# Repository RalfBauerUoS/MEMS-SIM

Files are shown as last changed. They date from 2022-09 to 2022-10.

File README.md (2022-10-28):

# MEMS-SIM
This repository is under construction and currently in development.

In the folders are details about the material list and costs to build a MEMS-SIM microscope as described in this BioRxiv preprint:  [https://www.biorxiv.org/content/10.1101/2022.09.12.507543v1](https://www.biorxiv.org/content/10.1101/2022.09.12.507543v1) 

Additionally there are 3D-designs, a basic control code specifically tailored to the MEMS used for the microscope and electronics diagram for the control.

## MEMS-SIM design
The below 3D-schematic shows the overall setup, excluting the lasers and sample stage.

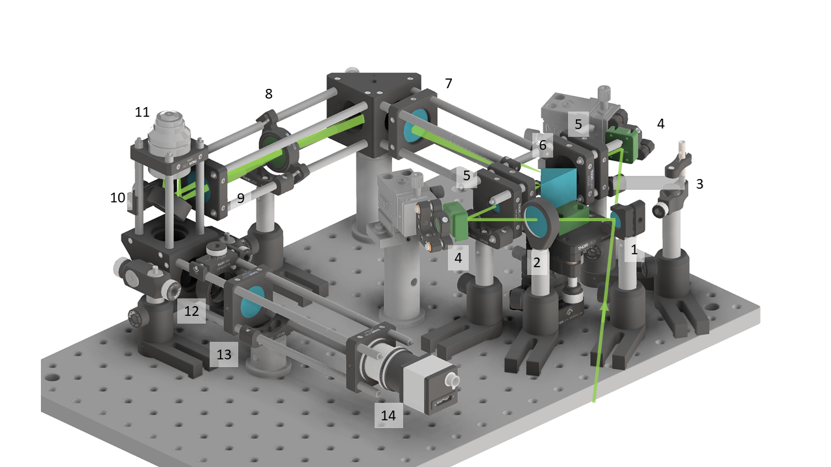
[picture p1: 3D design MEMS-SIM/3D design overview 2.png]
3D design overview


The 3D parts and full assembly of the shown setup are available in Autodesk Inventor format under the [3D design MEMS-SIM folder]

## Part list
The part list and costs (accurate as of September 2022) can be found in [this pdf](https://github.com/RalfBauerUoS/MEMS-SIM/blob/3ace88392d8fb00135eca98648ba5507b43cb822/MEMS-SIM%20-%20component%20list%20and%20costs.pdf)

## Electronics
An overview schematics of the electronics required to drive the two MEMS micromirror of the MEMS-SIM setup can be found [here](https://github.com/RalfBauerUoS/MEMS-SIM/blob/3ace88392d8fb00135eca98648ba5507b43cb822/Electronics/MEMS-SIM_Electronics_overview.png).

## MEMS control
The tip, tilt and piston movement and positioning of the two MEMS micromirror is controlled using an Arduino micro and custom python code with GUI. Both can be found in the relevant sub-folder.

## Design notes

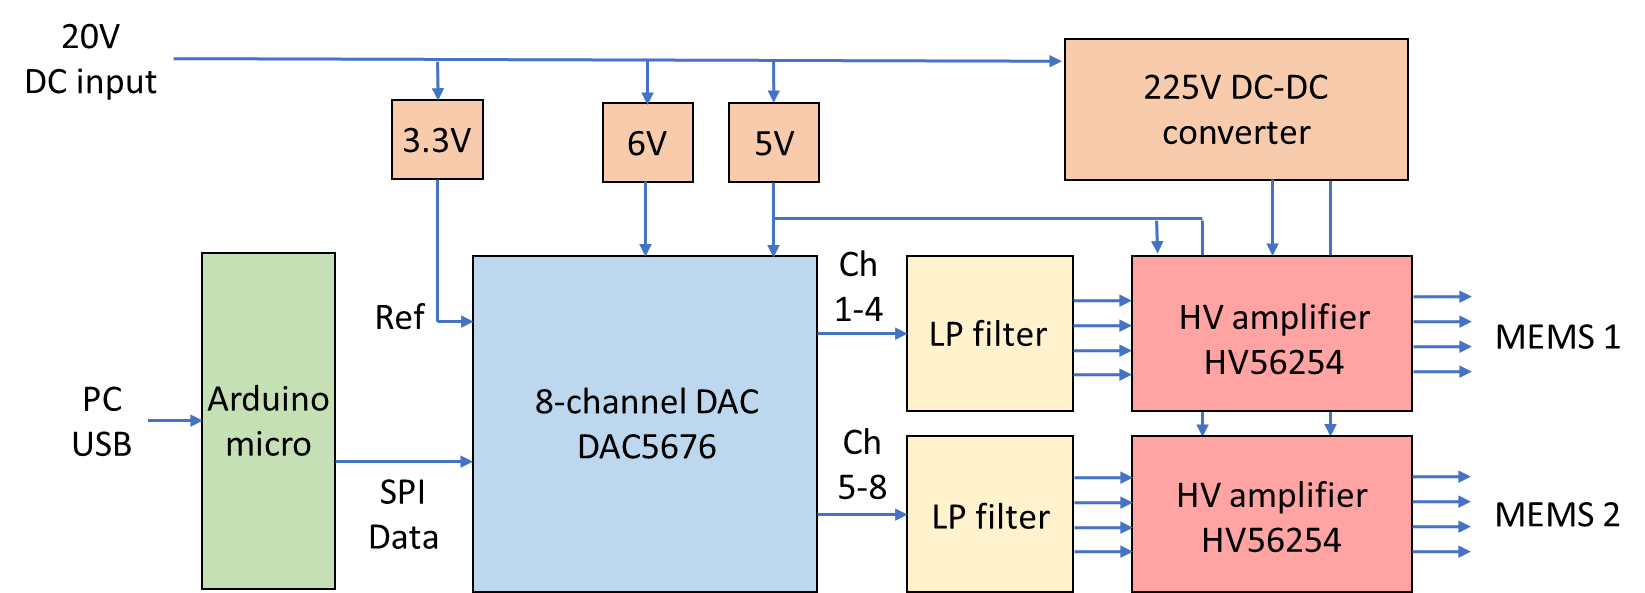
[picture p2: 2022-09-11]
Electronics/MEMS-SIM_Electronics_overview.png

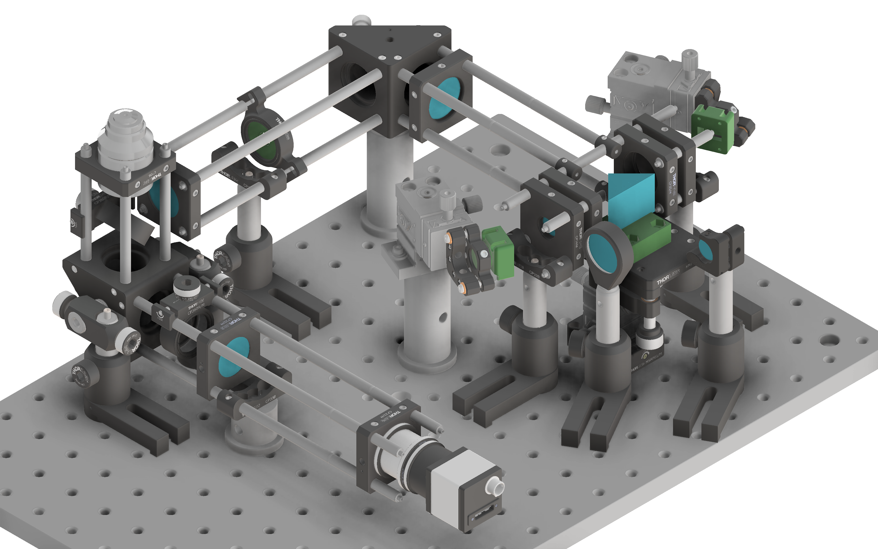
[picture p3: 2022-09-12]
3D design MEMS-SIM/SIMAssemlbly_v1.png

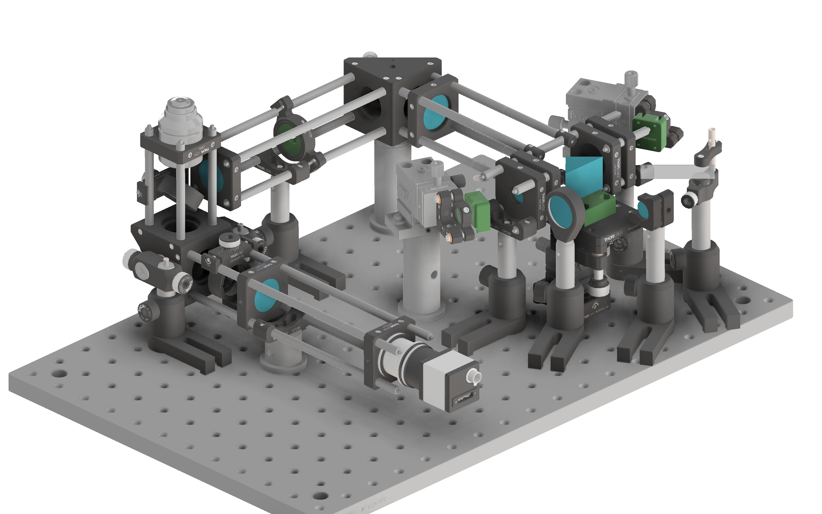
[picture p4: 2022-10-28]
3D design MEMS-SIM/SIMAssemlbly_v2.png

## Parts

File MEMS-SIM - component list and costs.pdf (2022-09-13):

MEMS SIM costs

No | Supplier | Item | Description | number item price | overall price
1 Odicforce | OFL17-F2 | 150mW 532nm laser module | 1 | 40.83 £ | 40.83 £
2 Lasever Inc | LSR473NL-50-PS-II | 50mW 473nm diode pumped solid state laser | 1 | 490.83 £ | 490.83 £
3 Mirrorcle | A7M20.2-2000AL | 2mm MEMS mirror | 2 | 429.17 £ | 858.33 £
4 Edmund Optics #13-821 | 100x 1.25NA Zeiss A-Plan Oil Immersion Objective | 1 | 593.00 £ | 593.00 £
5 IDS | UI-3060-CP-M-GL Rev.2 | IDS CMOS camera 1936x1216px | 1 | 480.00 £ | 480.00 £
6 Chroma | DC/ZT375/473/532/635rpc-UF1 Dichroic filter (multiband) | 1 | 654.00 £ | 654.00 £
7 Chroma | 69401m | Emission filter (multiband) | 1 | 347.00 £ | 347.00 £
8 Thorlabs | MRAK25-P01 | Knife edge prism | 1 | 102.32 £ | 102.32 £
9 Thorlabs | BSW04 | 50/50 1/2" broadband beam splitter | 1 | 64.26 £ | 64.26 £
10 Thorlabs | NDL-10C-2 | Continuous variable ND filter | 1 | 65.51 £ | 65.51 £
11 Thorlabs | BCP4310 | Beamsplitter compensation plate, 5mm thick | 1 | 80.69 £ | 80.69 £
12 Thorlabs | AC127-030-A | f=30mm 1/2" lenses | 2 | 42.43 £ | 84.86 £
13 Thorlabs | AC254-125-A | f=125mm 1" lens | 1 | 62.39 £ | 62.39 £
14 Thorlabs | AC254-075-A | f=75mm 1" lens | 1 | 62.39 £ | 62.39 £
15 Edmund Optics #47-644 | f=175mm 1" tube lens | 1 | 90.10 £ | 90.10 £
16 Thorlabs | ME1-P01 | 1" Ag mirror | 2 | 24.00 £ | 48.00 £
17 Thorlabs | ME05-P01 | 1/2" Ag mirror | 3 | 13.13 £ | 39.39 £
18 Thorlabs | DMLP505T | 1/2" dichroic laser beam combiner | 1 | 94.01 £ | 94.01 £
19 Thorlabs | LPVISE2X2 | Economy polariser | 1 | 6.82 £ | 6.82 £
20 Thorlabs | KPZNFL5/M | Piezo z-stage | 1 | 1,182.93 £ | 1,182.93 £
21 Thorlabs | MT1A/M | Manual xy-stage | 2 | 326.11 £ | 652.22 £
22 Thorlabs | MT401/M | xy base plate | 1 | 18.83 £ | 18.83 £
23 Thorlabs | NFL5P2/M | z-stage angle bracket | 1 | 80.69 £ | 80.69 £
24 Thorlabs | DT12XYZ/M | MEMS 3-axis position stage | 2 | 252.06 £ | 504.12 £
25 Thorlabs | DT12XY/M | Knife edge prism 2-axis positioning stage | 1 | 153.89 £ | 153.89 £
26 Thorlabs | KM100B/M | Tip-Tilt platform for knife edge prism | 1 | 46.39 £ | 46.39 £
27 Thorlabs | MSRP01/M | Rotation mount for knife edge prism | 1 | 59.69 £ | 59.69 £
28 Thorlabs | RSP1/M | Rotation mount for linear polariser | 1 | 70.30 £ | 70.30 £
29 Thorlabs | KCB1C/M | Right angle cage mirror mounts | 2 | 110.47 £ | 220.94 £
30 Thorlabs | CP360R/M | 360deg pivot cage mirror mount | 1 | 78.00 £ | 78.00 £
31 Thorlabs | CP35/M | 1" optics cage plate | 5 | 15.08 £ | 75.40 £
32 Thorlabs | CP33/M | 1" threaded optics cage plate | 1 | 13.64 £ | 13.64 £
33 Thorlabs | CP36 | 1.2" optics cage plate | 1 | 16.97 £ | 16.97 £
34 Thorlabs | CP33B | Cage mounting bracket | 4 | 11.48 £ | 45.92 £
35 Thorlabs | CMT10 | SM1 thread to C-mount adapter | 1 | 16.97 £ | 16.97 £
36 Thorlabs | ER4-P4 | 4" long cage rods | 4 | 20.84 £ | 83.36 £
37 Thorlabs | ER3-P4 | 3" long cage rods | 1 | 19.37 £ | 19.37 £
38 Thorlabs | ER2-P4 | 2" long cage rods | 1 | 17.91 £ | 17.91 £
39 Thorlabs | ER1-P4 | 1" long cage rods | 1 | 14.83 £ | 14.83 £
40 Thorlabs | KM05/M | 1/2" 2-axis mirror holder | 6 | 30.13 £ | 180.78 £
41 Newport | U50-S | 1/2" 2-axis mirror holder clear edge | 1 | 63.00 £ | 63.00 £
42 Thorlabs | RS2.5P/M | 2.5" long 1" pedastal post | 2 | 23.50 £ | 47.00 £
43 Thorlabs | RS1P/M | 1" long 1" pedastal post | 1 | 18.72 £ | 18.72 £
44 Thorlabs | UPH40/M-P5 | Universal 1/2" post holder 5pack | 3 | 122.70 £ | 368.10 £
45 Thorlabs | RA90/M | 90deg 1/2" post clamps | 3 | 7.73 £ | 23.19 £
46 Thorlabs | TR50/M-P5 | 50mm long 1/2" post 5pack | 4 | 18.95 £ | 75.80 £
47 Thorlabs | TR20/M-P5 | 20mm long 1/2" post 5pack | 1 | 17.30 £ | 17.30 £
48 Thorlabs | MB2530/M | Breadboard | 1 | 109.81 £ | 109.81 £
49 Misc | 3D-prints | 3D-printed adapters for MEMS, stage, pinholes, etc | 1 | 16.14 £ | 16.14 £
50 RS | Arduinio Micro | Arduino Micro microcontroller | 1 | 17.88 £ | 17.88 £
51 Digikey | EVAL-AD5676RSDZ | 8-channel DAC evaluation board | 1 | 91.77 £ | 91.77 £
52 RS | HV56264 | 225V amplifier HV56264 | 2 | 60.63 £ | 121.26 £
53 RS | AC/DC adapter | 24V AC/DC adapter | 1 | 9.50 £ | 9.50 £
54 RS | AD8694ARZ | AD8694ARZ 5th order low pass filter | 2 | 2.57 £ | 5.14 £
55 RS | Misc | Voltage regulators, resistors, capacitors | 3 £ | 5.00 £ | 15.00
£ | 8,817.49

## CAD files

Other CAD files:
3D design MEMS-SIM/131030 - Mounting Cleat.ipt
3D design MEMS-SIM/134330 - fixed_world_metric.ipt
3D design MEMS-SIM/134332 - moving_world_134332.ipt
3D design MEMS-SIM/134333 - screw_134333.ipt
3D design MEMS-SIM/134334 - screw_holder_metric.ipt
3D design MEMS-SIM/134336 - guide_bush_134336.ipt
3D design MEMS-SIM/134337 - flat spring_134337.ipt
3D design MEMS-SIM/134338 - metal_knob_134338.ipt
3D design MEMS-SIM/134341 - unit_angle_bracket_screw.ipt
3D design MEMS-SIM/134342 - DT12 metric.iam
3D design MEMS-SIM/134364 - DT12 Adaptor plate metric.ipt
3D design MEMS-SIM/210312 - Mirrorcle MEMS mount for half inch v4.ipt
3D design MEMS-SIM/210505 - Prism adapter v3.ipt
3D design MEMS-SIM/210505 - Zeiss x100 objective mockup.ipt
3D design MEMS-SIM/220912 - 8mm aperture.ipt
3D design MEMS-SIM/AC127-030-A-Step.ipt
3D design MEMS-SIM/AC254-075-A-Step.ipt
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

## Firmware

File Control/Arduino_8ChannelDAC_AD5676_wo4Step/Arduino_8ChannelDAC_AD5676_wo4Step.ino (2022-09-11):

//Arduino controlled 8-channel DAC for 2 full thermal MEMS chip control
//8-channel DAC used is AD5676 EVAL board, which connects via SPI and chip having 24-bit data input
//16 data bits, 4 command bits and 4 address bits for all 8 channels (max value 65535)
//serial input form LabView, 47 characters for single mirror change instruction, example "<50000,00000,00000,00000,00000,00000,00000,00000>" 
//when getting automated data transfered for 3 angles 3 phases, this goes to 48*9 characters + 4 characters (number of exposures) + 4 characters (exposure time) + 4 characters (wait time) = 443 characters
//when getting automated data transfered for 1 angle 3 phases, this goes to 48*3 characters + 4 characters (number of exposures) + 4 characters (exposure time) + 4 characters (wait time) = 155 characters

//#include <Wire.h>
#include <SPI.h>
#define CS 8 //digital pin 8 as chip select for SPI
#define trigger_o 10 //trigger output on pin 10
#define RSET 2 //digital pin 2 as reset

SPISettings settingsA(10000000, MSBFIRST, SPI_MODE1);

//int ad5676_address = 0x55; //Address for board needs to be checked with i2c_scanner!!

const uint16_t numChars = 445; //max length of serial read
char receivedChars[numChars];

uint16_t expTime = 0;
uint16_t waitTime = 0;
uint16_t frameNo = 0;
uint16_t stepDelay = 300; //time for steps in 4 step position change in microseconds - overall 3*this time value for full pos change
uint16_t Pos1[8], Pos2[8], Pos3[8], Pos4[8], Pos5[8], Pos6[8], Pos7[8], Pos8[8], Pos9[8]; //integers to write to DAC
uint16_t CurrentPos[8] = {0,0,0,0,0,0,0,0}; //initialise previous channel values to 0
uint16_t receivedNo = 0;

boolean newData = false;

//================================================

void setup() {
  Serial.begin(115200);
  Serial.println("8-channel DAC AD5676EVAL");

//  Wire.begin(); //initiate i2c comms
  pinMode(CS, OUTPUT);
  SPI.begin();
  SPI.setBitOrder(MSBFIRST);
  digitalWrite(CS, HIGH);

  pinMode(RSET, OUTPUT);
  digitalWrite(RSET, HIGH);

  SPI.beginTransaction(settingsA);
  digitalWrite(CS, LOW);
  SPI.transfer(0b0111);
  SPI.transfer((0x00 >> 8) & 0xFF);
  SPI.transfer((0x01) & 0xFF);
  digitalWrite(CS, HIGH);

  pinMode(trigger_o, OUTPUT);
  digitalWrite(trigger_o, LOW);

  Serial.println(SERIAL_BUFFER_SIZE);

}

//================================================

void loop() {
  // serial read to get commandline input or input from Labview
  receivedNo = receivedWithMarkers();

  if (receivedNo == 47 && newData == true) //check if sent instructions are for single change of both mirrors
  {
    char * strtokIndx; //used by strtok as index
    strtokIndx = strtok(receivedChars, ","); Pos1[2] = atoi(strtokIndx);
    strtokIndx = strtok(NULL, ","); Pos1[3] = atoi(strtokIndx);
    strtokIndx = strtok(NULL, ","); Pos1[0] = atoi(strtokIndx);
    strtokIndx = strtok(NULL, ","); Pos1[1] = atoi(strtokIndx);
    strtokIndx = strtok(NULL, ","); Pos1[6] = atoi(strtokIndx);
    strtokIndx = strtok(NULL, ","); Pos1[7] = atoi(strtokIndx);
    strtokIndx = strtok(NULL, ","); Pos1[4] = atoi(strtokIndx);
    strtokIndx = strtok(NULL, ","); Pos1[5] = atoi(strtokIndx);
    //order of Pos1 allocation changed to map physical output channels on MEMS correctly

    writeToDAC(Pos1);
   // Serial.println("single");
  }
  if (receivedNo == 155 && newData == true) // check if sent instructions are for automated run with only 1 angle
  {
    char * strtokIndx; //used by strtok as index
    strtokIndx = strtok(receivedChars, ","); Pos1[2] = atoi(strtokIndx);
    strtokIndx = strtok(NULL, ","); Pos1[3] = atoi(strtokIndx);
    strtokIndx = strtok(NULL, ","); Pos1[0] = atoi(strtokIndx);
    strtokIndx = strtok(NULL, ","); Pos1[1] = atoi(strtokIndx);
    strtokIndx = strtok(NULL, ","); Pos1[6] = atoi(strtokIndx);
    strtokIndx = strtok(NULL, ","); Pos1[7] = atoi(strtokIndx);
    strtokIndx = strtok(NULL, ","); Pos1[4] = atoi(strtokIndx);
    strtokIndx = strtok(NULL, ","); Pos1[5] = atoi(strtokIndx);
    strtokIndx = strtok(NULL, ","); Pos2[2] = atoi(strtokIndx);
    strtokIndx = strtok(NULL, ","); Pos2[3] = atoi(strtokIndx);
    strtokIndx = strtok(NULL, ","); Pos2[0] = atoi(strtokIndx);
    strtokIndx = strtok(NULL, ","); Pos2[1] = atoi(strtokIndx);
    strtokIndx = strtok(NULL, ","); Pos2[6] = atoi(strtokIndx);
    strtokIndx = strtok(NULL, ","); Pos2[7] = atoi(strtokIndx);
    strtokIndx = strtok(NULL, ","); Pos2[4] = atoi(strtokIndx);
    strtokIndx = strtok(NULL, ","); Pos2[5] = atoi(strtokIndx);
    strtokIndx = strtok(NULL, ","); Pos3[2] = atoi(strtokIndx);
    strtokIndx = strtok(NULL, ","); Pos3[3] = atoi(strtokIndx);
    strtokIndx = strtok(NULL, ","); Pos3[0] = atoi(strtokIndx);
    strtokIndx = strtok(NULL, ","); Pos3[1] = atoi(strtokIndx);
    strtokIndx = strtok(NULL, ","); Pos3[6] = atoi(strtokIndx);
    strtokIndx = strtok(NULL, ","); Pos3[7] = atoi(strtokIndx);
    strtokIndx = strtok(NULL, ","); Pos3[4] = atoi(strtokIndx);
    strtokIndx = strtok(NULL, ","); Pos3[5] = atoi(strtokIndx);
    strtokIndx = strtok(NULL, ","); frameNo = atoi(strtokIndx);
    strtokIndx = strtok(NULL, ","); expTime = atoi(strtokIndx);
    strtokIndx = strtok(NULL, ","); waitTime = atoi(strtokIndx);

    writeToDAC(Pos1);
    for (int u=0;u<8;u++)
    {
      CurrentPos[u] = Pos1[u];
    }
    
    Serial.println("1-position");
    
    for (int i=0;i<frameNo;i++)
    {
      writeToDAC(Pos1);
      delay(waitTime);
      digitalWrite(trigger_o, HIGH);
      delayMicroseconds(100);
      digitalWrite(trigger_o, LOW);
      delay(expTime);
      
      writeToDAC(Pos2);
      delay(waitTime);
      digitalWrite(trigger_o, HIGH);
      delayMicroseconds(100);
      digitalWrite(trigger_o, LOW);
      delay(expTime);
      
      writeToDAC(Pos3);
      delay(waitTime);
      digitalWrite(trigger_o, HIGH);
      delayMicroseconds(100);
      digitalWrite(trigger_o, LOW);
      delay(expTime);
    }
  }
  if (receivedNo == 443 & newData == true) //check if sent instructions are for automated operation with all 3 angles
  {
    char * strtokIndx; //used by strtok as index
    strtokIndx = strtok(receivedChars, ","); Pos1[2] = atoi(strtokIndx);
    strtokIndx = strtok(NULL, ","); Pos1[3] = atoi(strtokIndx);
    strtokIndx = strtok(NULL, ","); Pos1[0] = atoi(strtokIndx);
    strtokIndx = strtok(NULL, ","); Pos1[1] = atoi(strtokIndx);
    strtokIndx = strtok(NULL, ","); Pos1[6] = atoi(strtokIndx);
    strtokIndx = strtok(NULL, ","); Pos1[7] = atoi(strtokIndx);
    strtokIndx = strtok(NULL, ","); Pos1[4] = atoi(strtokIndx);
    strtokIndx = strtok(NULL, ","); Pos1[5] = atoi(strtokIndx);
    strtokIndx = strtok(NULL, ","); Pos2[2] = atoi(strtokIndx);
    strtokIndx = strtok(NULL, ","); Pos2[3] = atoi(strtokIndx);
    strtokIndx = strtok(NULL, ","); Pos2[0] = atoi(strtokIndx);
    strtokIndx = strtok(NULL, ","); Pos2[1] = atoi(strtokIndx);
    strtokIndx = strtok(NULL, ","); Pos2[6] = atoi(strtokIndx);
    strtokIndx = strtok(NULL, ","); Pos2[7] = atoi(strtokIndx);
    strtokIndx = strtok(NULL, ","); Pos2[4] = atoi(strtokIndx);
    strtokIndx = strtok(NULL, ","); Pos2[5] = atoi(strtokIndx);
    strtokIndx = strtok(NULL, ","); Pos3[2] = atoi(strtokIndx);
    strtokIndx = strtok(NULL, ","); Pos3[3] = atoi(strtokIndx);
    strtokIndx = strtok(NULL, ","); Pos3[0] = atoi(strtokIndx);
    strtokIndx = strtok(NULL, ","); Pos3[1] = atoi(strtokIndx);
    strtokIndx = strtok(NULL, ","); Pos3[6] = atoi(strtokIndx);
    strtokIndx = strtok(NULL, ","); Pos3[7] = atoi(strtokIndx);
    strtokIndx = strtok(NULL, ","); Pos3[4] = atoi(strtokIndx);
    strtokIndx = strtok(NULL, ","); Pos3[5] = atoi(strtokIndx);
    strtokIndx = strtok(NULL, ","); Pos4[2] = atoi(strtokIndx);
    strtokIndx = strtok(NULL, ","); Pos4[3] = atoi(strtokIndx);
    strtokIndx = strtok(NULL, ","); Pos4[0] = atoi(strtokIndx);
    strtokIndx = strtok(NULL, ","); Pos4[1] = atoi(strtokIndx);
    strtokIndx = strtok(NULL, ","); Pos4[6] = atoi(strtokIndx);
    strtokIndx = strtok(NULL, ","); Pos4[7] = atoi(strtokIndx);
    strtokIndx = strtok(NULL, ","); Pos4[4] = atoi(strtokIndx);
    strtokIndx = strtok(NULL, ","); Pos4[5] = atoi(strtokIndx);
    strtokIndx = strtok(NULL, ","); Pos5[2] = atoi(strtokIndx);
    strtokIndx = strtok(NULL, ","); Pos5[3] = atoi(strtokIndx);
    strtokIndx = strtok(NULL, ","); Pos5[0] = atoi(strtokIndx);
    strtokIndx = strtok(NULL, ","); Pos5[1] = atoi(strtokIndx);
    strtokIndx = strtok(NULL, ","); Pos5[6] = atoi(strtokIndx);
    strtokIndx = strtok(NULL, ","); Pos5[7] = atoi(strtokIndx);
    strtokIndx = strtok(NULL, ","); Pos5[4] = atoi(strtokIndx);
    strtokIndx = strtok(NULL, ","); Pos5[5] = atoi(strtokIndx);
    strtokIndx = strtok(NULL, ","); Pos6[2] = atoi(strtokIndx);
    strtokIndx = strtok(NULL, ","); Pos6[3] = atoi(strtokIndx);
    strtokIndx = strtok(NULL, ","); Pos6[0] = atoi(strtokIndx);
    strtokIndx = strtok(NULL, ","); Pos6[1] = atoi(strtokIndx);
    strtokIndx = strtok(NULL, ","); Pos6[6] = atoi(strtokIndx);
    strtokIndx = strtok(NULL, ","); Pos6[7] = atoi(strtokIndx);
    strtokIndx = strtok(NULL, ","); Pos6[4] = atoi(strtokIndx);
    strtokIndx = strtok(NULL, ","); Pos6[5] = atoi(strtokIndx);
    strtokIndx = strtok(NULL, ","); Pos7[2] = atoi(strtokIndx);
    strtokIndx = strtok(NULL, ","); Pos7[3] = atoi(strtokIndx);
    strtokIndx = strtok(NULL, ","); Pos7[0] = atoi(strtokIndx);
    strtokIndx = strtok(NULL, ","); Pos7[1] = atoi(strtokIndx);
    strtokIndx = strtok(NULL, ","); Pos7[6] = atoi(strtokIndx);
    strtokIndx = strtok(NULL, ","); Pos7[7] = atoi(strtokIndx);
    strtokIndx = strtok(NULL, ","); Pos7[4] = atoi(strtokIndx);
    strtokIndx = strtok(NULL, ","); Pos7[5] = atoi(strtokIndx);    
    strtokIndx = strtok(NULL, ","); Pos8[2] = atoi(strtokIndx);
    strtokIndx = strtok(NULL, ","); Pos8[3] = atoi(strtokIndx);
    strtokIndx = strtok(NULL, ","); Pos8[0] = atoi(strtokIndx);
    strtokIndx = strtok(NULL, ","); Pos8[1] = atoi(strtokIndx);
    strtokIndx = strtok(NULL, ","); Pos8[6] = atoi(strtokIndx);
    strtokIndx = strtok(NULL, ","); Pos8[7] = atoi(strtokIndx);
    strtokIndx = strtok(NULL, ","); Pos8[4] = atoi(strtokIndx);
    strtokIndx = strtok(NULL, ","); Pos8[5] = atoi(strtokIndx);
    strtokIndx = strtok(NULL, ","); Pos9[2] = atoi(strtokIndx);
    strtokIndx = strtok(NULL, ","); Pos9[3] = atoi(strtokIndx);
    strtokIndx = strtok(NULL, ","); Pos9[0] = atoi(strtokIndx);
    strtokIndx = strtok(NULL, ","); Pos9[1] = atoi(strtokIndx);
    strtokIndx = strtok(NULL, ","); Pos9[6] = atoi(strtokIndx);
    strtokIndx = strtok(NULL, ","); Pos9[7] = atoi(strtokIndx);
    strtokIndx = strtok(NULL, ","); Pos9[4] = atoi(strtokIndx);
    strtokIndx = strtok(NULL, ","); Pos9[5] = atoi(strtokIndx);    
    strtokIndx = strtok(NULL, ","); frameNo = atoi(strtokIndx);
    strtokIndx = strtok(NULL, ","); expTime = atoi(strtokIndx);
    strtokIndx = strtok(NULL, ","); waitTime = atoi(strtokIndx);

    writeToDAC(Pos1);
    for (int u=0;u<8;u++)
    {
      CurrentPos[u] = Pos1[u];
    }
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
